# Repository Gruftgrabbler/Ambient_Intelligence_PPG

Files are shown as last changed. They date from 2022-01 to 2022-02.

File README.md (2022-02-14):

# Venen Funktionsmessung mittels PPG
Bei der venösen Photoplethysmographie wird die Lichtreflexion (Synonym: Licht-Reflexions-Rheographie, LRR)
mittels eines PPG-Sensors gemessen. Da Licht von Blut stärker als vom Gewebe absorbiert wird, nimmt
die Lichtreflexion bei steigendem Blutvolumen im Bein ab. Das LRR-Signal spiegelt daher Blutvolumenschwankungen wider.
Das LRR-Signal gliedert sich in einen gleich bleibenden Anteil durch Lichtabsorption in nicht-durchblutetem Gewebe 
(ca. 90 %), eine variable Lichtabsorption durch das venöse Blutvolumen (ca. 10 %) und eine periodische arterielle 
Lichtabsorption (ca. 0,5 %). Mithilfe digitaler Filtertechniken können diese Signale voneinander getrennt werden 
(digitale Photoplethysmographie, dPPG) [[1]](https://docplayer.org/21805396-Phlebologische-funktionsdiagnostik.html).

## Durchführung der Messung

Der sitzende Patient führt acht Dorsalextensionen im Sprunggelenk innerhalb von 16 Sekunden im Metronomrhythmus durch. Die Ferse ist dabei am Boden
abgestützt. Der PPG-Sensor wird mithilfe des 3D gedruckten Gehäuses ca. 10 cm oberhalb des Malleolus medialis angebracht (Abbildung 1). 

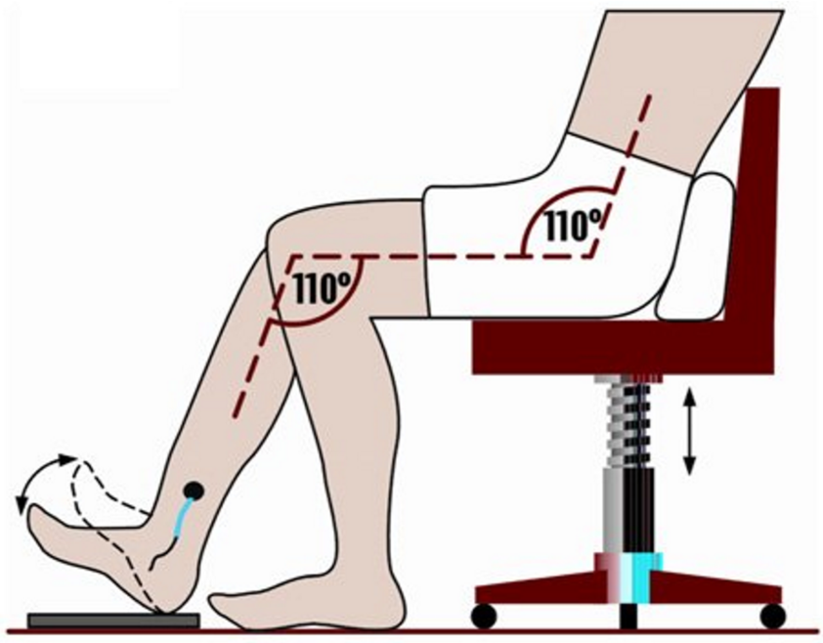
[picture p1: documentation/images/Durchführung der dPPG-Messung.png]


**Abbildung 1:** empfohlene Körperhaltung während der Messdurchführung [[2]](https://www.researchgate.net/publication/6482990_Photoplethysmography_and_its_application_in_clinical_physiological_measurement)

Die Fußbewegung führt zur Kompression der Beinvenen und damit zu einem Bluttransport nach proximal (Muskelpumpe). Das abnehmende Blutvolumen
spiegelt sich in der LRR-Kurve durch eine zunehmende Lichtreflexion wider (Abbildung 2). Nach Beendigung der Fußbewegungen fließt das 
Blut wieder nach distal. Bei insuffizienten Venen geschieht das schneller, als bei suffizienten Venenklappen 
[[1]](https://docplayer.org/21805396-Phlebologische-funktionsdiagnostik.html).

Mustermessung

**Abbildung 2:** LRR-Kurve mit zunehmender Lichtreflexion während der Fußbewegungen  [[3]](https://link.springer.com/chapter/10.1007/978-3-642-23804-8_36)[[4]](https://link.springer.com/chapter/10.1007/978-3-642-01709-4_35)

Der Messzyklus läuft vollautomatisch ab, die Messsignale werden ebenfalls automatisch ausgewertet.
Erfasst werden folgende Parameter zur unterstützenden Diagnostik der Venenfunktion:
* Venöse Wiederauffüllzeit 
* Venöse Halbwertszeit 
* Initiale Auffüllzeit 
* Venöse Pumpleistung 
* Venöse Pumparbeit 

## Konfiguration des MAX30102-Sensors

Der MAX30102 PPG-Sensor enthält zwei Leuchtdioden (LEDs), eine infrarote LED (Spitzenwellenlänge 880 nm) und eine rote LED (Spitzenwellenlänge 660 nm); dazu kommt eine Fotodiode, die spezifisch für Wellenlängen zwischen 600 und 900 nm ausgelegt ist. Im MAX30102 Sensor ist ein integrierter Temperatursensor zur Messung von Temperaturschwankungen, ein Analog-Digital Wandler (ADC) und eine I2C-Schnittstelle. Durch die Integration des ADC und der I2C-Schnittstelle in den Sensor selbst werden Rauschen und Artefakte, die zwischen der Fotodiode und dem ADC entstehen, auf ein Minimum reduziert. Die Daten werden über eine serielle Verbindung vom ESP32 an den angeschlossenen PC übertragen. Der PPG-Sensor wurde auf eine Abtastrate von 20 Hz konfiguriert, wobei die in Tabelle 1 aufgeführten Einstellungen verwendet wurden.

**Tabelle 1:** Empfohlene Einstellungen zur Konfiguration des MAX30102-Sensors
|    Setting    |      Value     | Description                                                                                                                        |
|---------------|:--------------:|------------------------------------------------------------------------------------------------------------------------------------|
| ledBrightness | 0x66 (= 20 mA) | Wertebereich (Hex-Dec=LED-Strom): 0-0=0mA (Off) to 0xFF-255=50mA <br /> 0x33-51=10mA. 0x66-102=20mA. 0x99-153=30mA. 0xCC-204=40mA  |
| sampleAverage |        4       | Averages multiple samples then draw once, reduce data throughput, default 4 samples average                                        |
| ledMode       |        1       | 1 = Red only, 2 = Red + IR, 3 = Red + IR + Green                                                                                   |
| sampleRate    |      1000      | Valid options: 50, 100, 200, 400, 800, 1000, 1600, 3200                                                                            |
| pulseWidth    |       411      | Valid options: 69, 118, 215, 411. The longer the pulse width, the wider the detection range. Default to be Max range               |
| adcRange      |      2048      | ADC Measurement Range, default 4096 (nA)，15.63(pA) per LSB at 18 bits resolution                                                  |

Die aufgeführten Werte wurden anhand des Datenblatts zum MAX30102 Sensor ermittelt und experimentell anhand einer ausreichenden Signalqualität bestätigt [[5]](https://pdfserv.maximintegrated.com/en/an/AN6409.pdf).

Bei der LRR-Messung wird die variable Lichtabsorption durch Schwankungen im venösen Blutvolumen gemessen. Daher ist für die Aufzeichnung der LRR-Kurve hauptsächlich das desoxygenierte Blut, bzw. die Absorption des Lichts durch desoxygenierte Hämoglobin von Relevanz. Dieses weist seine höchste Absorption im Wellenlängenbereich von 660-680 nm auf.
Aus diesem Grund wird für die LRR-Messung nur die rote LED des MAX30102 Sensors verwendet.

Abbildung 3 zeigt die zulässigen Einstellungen für die Messung der Blutvolumenschwankungen im Einzel-LED-Modus (Herzfrequenzmodus). Im Herzfrequenzmodus wird nur die rote LED verwendet, um optische Daten zu erfassen und die Herzfrequenz und/oder das Photoplethysmogramm (PPG) des Patienten zu bestimmen. Die grau hinterlegten Felder entsprechen den Einstellungen, die nicht zulässig sind. Der Benutzer sollte die Impulsbreite und die Abtastungen pro Sekunde anpassen, um die besten Einstellungen für seine Anwendung und den zulässigen Energieverbrauch zu ermitteln.

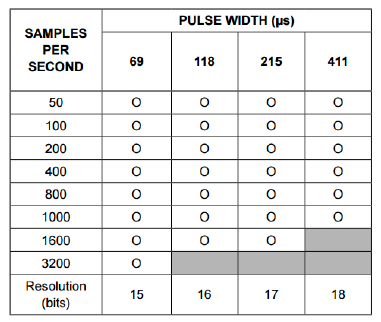
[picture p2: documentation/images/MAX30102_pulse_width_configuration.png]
pulse_width_configuration


**Abbildung 3:** Zulässige Einstellungen für die Pulsweiten-Konfiguration im Einzel-LED Betrieb (Herzfrequenzmodus). [[5]](https://pdfserv.maximintegrated.com/en/an/AN6409.pdf)

Die Pulsweite gibt an, wie lange das Abtastsignal aktiv ist. Je länger das Signal aktiv bleibt, desto mehr Energie wird verbraucht. Die Ansteuerungsfrequenz für die LEDs wird durch die Abtastrate bestimmt. Eine höhere Abtastrate führt zu einer höheren Ansteuerungsfrequenz und damit zu einem höheren Energieverbrauch. Die ideale Option für eine Wearable-Anwendung ist die Wahl einer geringeren Pulsbreite in Kombination mit einer geringeren Abtastrate, um den Energieverbrauch zu minimieren. Dies funktioniert jedoch nur bis zu einer gewissen Grenze, da die Pulsweite in einem umgekehrten Verhältnis zur Abtastrate steht. Dies ergibt sich aus der Überlegung, dass eine höhere Impulsbreite einer niedrigeren Antriebsfrequenz entspricht und umgekehrt. 

In unserem Anwendungsfall ist der Energieverbrauch des Sensors unerheblich, da der Sensor nicht in einer Wearable-Anwendung mit begrenzter Energieversorgung eingesetzt wird, sondern über die Energiezufuhr vom ESP32 bzw. vom PC gespeist wird. 

Im Datenblatt zu den empfohlenen Konfigurationen zum Betrieb des MAX30102 wird empfohlen, den ADC auf seinen höchsten Gain (= Verstärkungseinstellung) zu setzen (full-scale range = 2,048 μA). Wenn der Kanal gesättigt ist, muss die Verstärkungseinstellung auf den nächst höheren Wert eingestellt werden. [[6]](https://www.maximintegrated.com/en/products/interface/sensor-interface/MAX30102.html)

Der Sensor wird zur Befestigung am Bein in einem 3D gedruckten Gehäuse untergebracht (Abbildung 4). Anschließend wird ein Klettverschlussband oder ein dehnfähiges Band durch die Halterungsschlaufe hindurchgeführt und der Sensor wie in der Versuchsdurchführung beschrieben am Bein befestigt. Hierbei ist auf einen lockeren und nicht zu festen Anpressdruck zu achten!

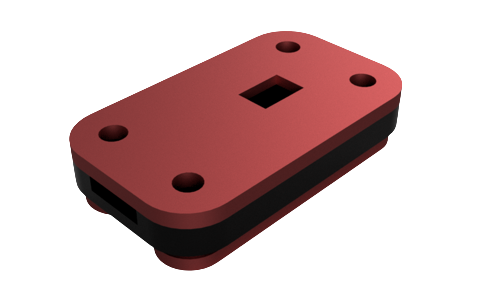
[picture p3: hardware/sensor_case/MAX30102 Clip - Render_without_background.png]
MAX30102 Clip - Render


**Abbildung 4:** Rendering des CAD Designs vom MAX30102 Clip zur Befestigung am Bein.

## Datenaufnahme
Zur Aufnahme und Speicherung der seriell übertragenen Messwerte durch den ESP32 wurde ein Python-Skript geschrieben (`real_time_plotter.py`). Der Python-Code erfasst die Daten und stellt diese in einem Echtzeit-Plotter grafisch dar. Zeitgleich werden die Messwerte direkt nach dem Empfang in einer *.csv-Datei gespeichert, was als Grundlage der nachfolgenden Analyse dient. 
Der Grund für die umgehende Datensicherung liegt in der hohen Eingangsgeschwindigkeit der Daten, welche mit einer Aufnahmefrequenz von 20 Hz eintreffen. Um die Datenverarbeitung zwischen den seriellen Erfassungen auf ein Minimum zu reduzieren, findet die weitere Datenverarbeitung nicht in Echtzeit, sondern im Anschluss an die Messung anhand der aufgezeichneten Messwerte in der csv-Datei statt.

## Vorverarbeitung der Daten
Für den Import der Messdaten aus der resultierenden CSV-Datei und die anschließende Datenverarbeitung zur Analyse wurde ein zweites Skript geschrieben (`plot_csv.py`). Der erste Schritt bei der Verarbeitung der LRR-Daten besteht darin, die Basislinie unserer Messdaten zu ermitteln. Hierfür betrachten wir die Ableitung erster Ordnung und ermitteln den Startzeitpunkt der Fußbewegungen anhand des Kurvenanstiegs über einen experimentell ermittelten Grenzwert hinaus. Der letzte Zeitpunkt vor dem Überschreiten des Grenzwerts wird als Startzeitpunkt der Messdurchführung definiert, die zugehörige Signalamplitude als Basislinie.

Im nächsten Schritt werden die Daten durch einen Tiefpass 4. Ordnung gefiltert. Die untere Grenzfrequenz wurde auf 3 Hz gewählt, um die Gleichstromkomponente der Daten zu entfernen. Anschließend werden die Zeitpunkte und Amplituden der lokalen Maxima mit der in Scipy integrierten Funktion *findpeaks* ermittelt. Für die weitere Analyse ist nur der zuletzt aufgetretene Höhepunkt nach Belastungsstop  von Relevanz. In Abbildung 5 ist eine Messdurchführung mit relevanten Punkten für die weitere Analyse dargestellt.

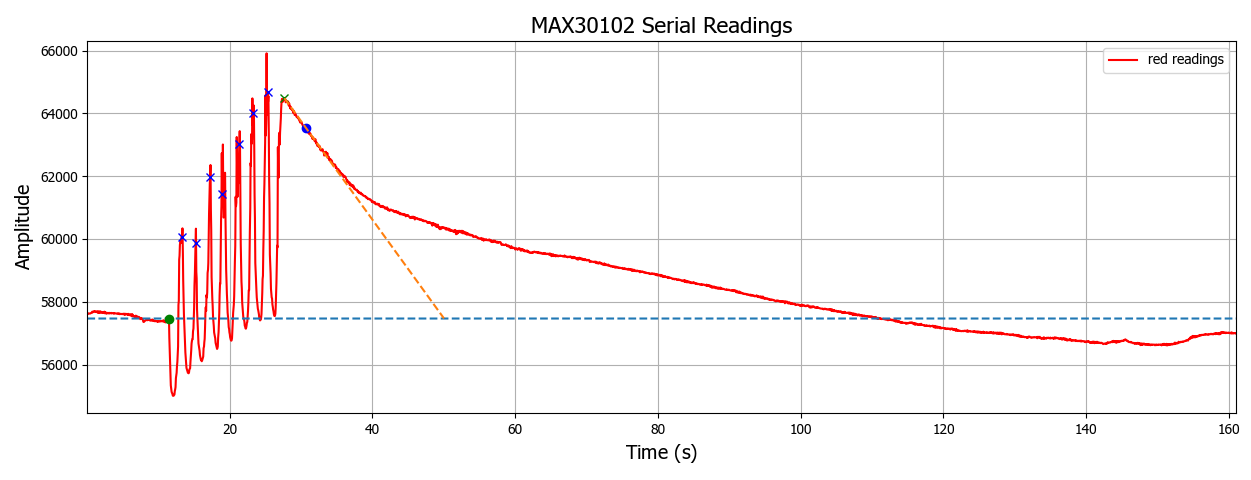
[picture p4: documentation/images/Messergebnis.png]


**Abbildung 5:** Messdurchführung mit relevanten Punkten

## Auswertung der Messergebnisse 
Die Berechnung der erfassten Messparameter ist der Fachliteratur entnommen [[7]](https://www.thieme-connect.de/products/ebooks/lookinside/10.1055/b-0034-8814)[[8]](https://eref.thieme.de/cockpits/clNuN0001clHAM0004/0/coNuN00260/4-910)[[9]](http://www.medpool.ch/geschuetzt/ch_seiten/med_300_/med_s123.htm)[[10]](http://docplayer.org/19942299-Dynamische-venenfunktionstests-auf-dem-pruefstand.html):

1. Aus dem Zeitintervall zwischen  und dem Ende des Kurvenabfalls am Schnittpunkt mit der Basislinie ergibt sich die venöse Auffüllzeit.

2. Aus dem Zeitintervall zwischen  und dem Unterschreiten von 50% der Amplitude von  ergibt sich die venöse Halbwertszeit.

3. Eine Gerade zwischen  und dem Kurvenpunkt nach drei Sekunden Abfall wird bis zur Basislinie verlängert und ergibt dort im Schnittpunkt die initiale Auffüllzeit.

4. Die venöse Pumpleistung folgt aus der Signalamplitude, nachdem die Signalamplitude mit der Amplitude der Basislinie normiert wurde:

      

5. Die venöse Pumparbeit wird durch Integration der venösen Pumpleistung über das Zeitintervall zwischen  und dem Ende des Kurvenabfalls am Schnittpunkt mit der Basislinie ermittelt.

In Tabelle 2 sind die ermittelten quantitativen Parameter für das Messsignal in Abbildung 5 gelistet.

**Tabelle 2:** ermittelte Parameter aus der automatisierten Analyse der aufgezeichneten Messwerte 
| Quantitative Parameter        | Messwerte |
|-------------------------------|:---------:|
| Venöse Auffüllzeit T_0 (s)    |    83.157 |
| Venöse Halbwertszeit T_50 (s) |    14.098 |
| Initiale Auffüllzeit T_i (s)  |    22.357 |
| Venöse Pumpleistung V_0 (%)   |    12.203 |
| Venöse Pumparbeit F_0 (%s)    |   311.642 |

# Setup

## Hardware

* Adafruit HUZZAH32 – ESP32 Feather Board oder ein alternativer Microcontroller mit I2C-Bus Ansteuerung
* MAX30102 Heart Rate/SpO2 Sensor
* 3D gedrucktes Gehäuse zur Befestigung des Sensors am Bein

## Software

* SparkFun MAX3010x Sensor Library für die Datenaufnahme
* Python 3.8 für die weitere Datenverarbeitung

## Getting Started

Stelle zunächst sicher, dass Python 3.8 auf dem Rechner installiert ist.

1. Best practice: Erstelle ein neues Virtual Environment, beispielsweise unter Verwendung von Anaconda oder PyCharm
2. Pullen des Repository einschließlich der Submodule: `git submodule update --init --recursive`
3. Installiere die Projekt-Requirements mittels pip: `pip install -r requirements.txt`

### Anleitung zur Messdurchführung
1. Drucke das Gehäuse des PPG-Sensors mit einem 3D-Drucker aus und setze den MAX30102-Sensor ein. Führe anschließend ein Klettverschlussband oder ein dehnfähiges Band durch die Halterungsschlaufe hindurch und befestige den Sensor wie in der Versuchsdurchführung beschrieben am Bein. Hierbei ist auf einen lockeren und nicht zu festen Anpressdruck zu achten!
2. Stelle eine Hardware Verbindung zwischen dem MAX30102-Sensor und dem ESP32 her
3. Flashe den ESP32 mit der *MAX30102_Basic_Readings.ino* im Projektordner *embedded/arduino-sketches/MAX30102_Basic_Readings/*
4. Führe das Skript `real_time_plotter.py` im Projektordner *src/serial/serial_plotter/* in der Python IDE deiner Wahl aus. Es öffnet sich eine GUI mit den Messsignalen der roten und infraroten LEDs. Zur problemlosen Analyse der Messdaten wird empfohlen, dass nur ein einziger vollständiger Messdurchgang pro csv-Datei gespeichert wird. Dies wird durch Beenden des Skripts nach Abschluss der Messung erreicht.
5. Führe zur Bestimmung der diagnostisch relevanten quantitativen Parameter das Skript `lrr_signal_evaluation.py` im *src/* Ordner aus. Sofern die Messung vorher korrekt durchgeführt wurde, gibt das Skript die gesuchten Parameter in der Konsole aus und stellt das Messsignal mitsamt einigen relevanten Punkten grafisch dar.

# Literaturverzeichnis

[[1]](https://docplayer.org/21805396-Phlebologische-funktionsdiagnostik.html) Stücker, M. & Doerler, M. (2014). Phlebological functional diagnostics. Phlebologie, 43(05), 268–272. https://doi.org/10.12687/phleb2213-5-2014

[[2]](https://www.researchgate.net/publication/6482990_Photoplethysmography_and_its_application_in_clinical_physiological_measurement) Allen, John. (2007). Photoplethysmography and its application in clinical physiological measurement. Physiological Measurement. 28. R1-39. https://doi.org/10.1088/0967-3334/28/3/R01

[[3]](https://link.springer.com/chapter/10.1007/978-3-642-23804-8_36) Noppeney T. (2013) Varikose. In: Jauch KW., Mutschler W., Hoffmann J., Kanz KG. (eds) Chirurgie Basisweiterbildung. Springer, Berlin, Heidelberg. https://doi.org/10.1007/978-3-642-23804-8_36

[[4]](https://link.springer.com/chapter/10.1007/978-3-642-01709-4_35) Noppeney T., Nüllen H. (2012) Varikose der unteren Extremität. In: Debus E., Gross-Fengels W. (eds) Operative und interventionelle Gefäßmedizin. Springer, Berlin, Heidelberg. https://doi.org/10.1007/978-3-642-01709-4_35

[[5]](https://pdfserv.maximintegrated.com/en/an/AN6409.pdf) MAX3010x EV Kits: Recommended Configurations and Operating Profiles. (2018b, Juni 27). Maxim Integrated - Analog, Linear, and Mixed-Signal Devices. Abgerufen am 9. Februar 2022, von https://www.maximintegrated.com/en/design/technical-documents/userguides-and-manuals/6/6409.html

[[6]](https://www.maximintegrated.com/en/products/interface/sensor-interface/MAX30102.html) MAX30102 High-Sensitivity Pulse Oximeter and Heart-Rate Sensor for Wearable Health. (2020, 13. Februar). Maxim Integrated - Analog, Linear, and Mixed-Signal Devices. Abgerufen am 9. Februar 2022, von https://www.maximintegrated.com/en/products/interface/sensor-interface/MAX30102.html

[[7]](https://www.thieme-connect.de/products/ebooks/lookinside/10.1055/b-0034-8814) Rabe, E. & Gerlach, H. E. (Hrsg.). (2006). 3.4 Photoplethysmographie. In: Praktische Phlebologie - Empfehlungen zur differenzierten Diagnostik und Therapie phlebologischer Krankheitsbilder, (2. vollständig überarbeitete Auflage Thieme Verlagsgruppe, Stuttgart, New York, Delhi, Rio), 38–40. https://doi.org/10.1055/b-0034-8814

[[8]](https://eref.thieme.de/cockpits/clNuN0001clHAM0004/0/coNuN00260/4-910) Ludwig M, Rieger J, Ruppert V. Auswertung. In: Ludwig M, Rieger J, Ruppert V, Hrsg. Gefäßmedizin in Klinik und Praxis. 2., komplett überarbeitete und aktualisierte Auflage. Stuttgart: Thieme; 2010. https://doi.org/10.1055/b-002-10340

[[9]](http://www.medpool.ch/geschuetzt/ch_seiten/med_300_/med_s123.htm) Wosnitzka, H. (o. D.). PPG-Parameter bei CVI-Verlaufskontrolle – aus einer Pharmakotherapiestudie. medpool.ch. Abgerufen am 9. Februar 2022, von http://www.medpool.ch/geschuetzt/ch_seiten/med_300_/med_s123.htm

[[10]](http://docplayer.org/19942299-Dynamische-venenfunktionstests-auf-dem-pruefstand.html) Häfner, H. M., Bablich, H., Rassner, G., Jünger, M. & Steins, A. (2002). Dynamische Venenfunktionstests auf dem Prüfstand. Phlebologie, 31(04), 85–90. https://doi.org/10.1055/s-0037-1621393

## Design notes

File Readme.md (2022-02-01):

# Venen Funktionsmessung mittels PPG
Bei der venösen Photoplethysmographie wird die Lichtreflexion (Synonym: Licht-Reflexions-Rheographie, LRR)
mittels eines PPG-Sensors gemessen. Da Licht von Blut stärker als vom Gewebe absorbiert wird, nimmt
die Lichtreflexion bei steigendem Blutvolumen im Bein ab. Das PPG-Signal spiegelt daher Blutvolumenschwankungen wider.
Das PPG-Signal gliedert sich in einen gleich bleibenden Anteil durch Lichtabsorption in „undurchblutetem“ Gewebe 
(ca. 90 %), eine variable Lichtabsorption durch das venöse Blutvolumen (ca. 10 %) und eine periodische arterielle 
Lichtabsorption (ca. 0,5 %). Mithilfe digitaler Filtertechniken können diese Signale voneinander getrennt werden 
(digitale Photoplethysmographie, dPPG) [[1]](https://docplayer.org/21805396-Phlebologische-funktionsdiagnostik.html).

## Durchführung der Messung

Der sitzende Patient führt acht Dorsalextensionen im Sprunggelenk innerhalb von 16 Sekunden im Metronomrhythmus durch. Die Ferse ist dabei am Boden
abgestützt. Der PPG-Sensor wird mithilfe des 3D gedruckten Gehäuses ca. 10 cm oberhalb des Malleolus medialis angebracht (Abbildung 1). 



**Abbildung 1:** Empfohlene Körperhaltung während der Messdurchführung [[2]](https://www.researchgate.net/publication/6482990_Photoplethysmography_and_its_application_in_clinical_physiological_measurement)

Die Fußbewegung führt zur Kompression der Beinvenen und damit zu einem Bluttransport nach proximal (Muskelpumpe). Das abnehmende Blutvolumen
spiegelt sich in der PPG-Kurve durch eine zunehmende Lichtreflexion wider (Abbildung 2). Nach Beendigung der Fußbewegungen fließt das 
Blut wieder nach distal. Bei insuffizienten Venen geschieht das schneller, als bei suffizienten Venenklappen 
[[1]](https://docplayer.org/21805396-Phlebologische-funktionsdiagnostik.html).

Mustermessung

**Abbildung 2:** PPG-Kurve mit zunehmender Lichtreflexion während der Fußbewegungen  [[3]](https://link.springer.com/chapter/10.1007/978-3-642-23804-8_36)

Der Messzyklus läuft vollautomatisch ab, die Messsignale werden ebenfalls automatisch ausgewertet.
Erfasst werden folgende Parameter zur unterstützenden Diagnostik der Venenfunktion:
* Venöse Wiederauffüllzeit 
* Venöse Halbwertszeit 
* Initiale Auffüllzeit 
* Venöse Pumpleistung 
* Venöse Pumparbeit 

## Konfiguration des MAX30102-Sensors

Der MAX30102 PPG-Sensor enthält zwei Leuchtdioden (LEDs), eine infrarote LED (Spitzenwellenlänge 880 nm) und eine rote LED (Spitzenwellenlänge 660 nm); dazu kommt eine Photodiode, die spezifisch für Wellenlängen zwischen 600 und 900 nm ausgelegt ist. Im MAX30102 Sensor ist ein integrierter Temperatursensor zur Messung von Temperaturschwankungen, ein Analog-Digital Wandler (ADC) und eine I2C-Schnittstelle. Durch die Integration des ADC und der I2C-Schnittstelle in den Sensor selbst werden Rauschen und Artefakte, die zwischen der Fotodiode und dem ADC entstehen, auf ein Minimum reduziert. Die Daten werden über eine serielle Verbindung vom ESP32 an den angeschlossenen PC übertragen. Der PPG-Sensor wurde auf eine Abtastrate von 20 Hz konfiguriert, wobei die in Tabelle 1 aufgeführten Einstellungen verwendet wurden.

**Tabelle 1:** Empfohlene Einstellungen zur Konfiguration des MAX30102-Sensors
|    Setting    |      Value     | Description                                                                                                                        |
|---------------|:--------------:|------------------------------------------------------------------------------------------------------------------------------------|
| ledBrightness | 0x66 (= 20 mA) | Wertebereich (Hex-Dec=LED-Strom): 0-0=0mA (Off) to 0xFF-255=50mA <br /> 0x33-51=10mA. 0x66-102=20mA. 0x99-153=30mA. 0xCC-204=40mA  |
| sampleAverage |        4       | Averages multiple samples then draw once, reduce data throughput, default 4 samples average                                        |
| ledMode       |        3       | 1 = Red only, 2 = Red + IR, 3 = Red + IR + Green                                                                                   |
| sampleRate    |      1000      | Valid options: 50, 100, 200, 400, 800, 1000, 1600, 3200                                                                            |
| pulseWidth    |       411      | Valid options: 69, 118, 215, 411. The longer the pulse width, the wider the detection range. Default to be Max range               |
| adcRange      |      2048      | ADC Measurement Range, default 4096 (nA)，15.63(pA) per LSB at 18 bits resolution                                                  |

## Datenaufnahme
Zur Aufnahme und Speicherung der seriell übertragenen Messwerte durch den ESP32 wurde ein Python-Skript geschrieben (`real_time_plotter.py`). Der Python-Code erfasst die Daten und stellt diese in einem Echtzeit-Plotter graphisch dar. Zeitgleich werden die Messwerte direkt nach dem Empfang in einer .csv-Datei gespeichert, was als Grundlage der nachfolgenden Analyse dienst. 
Der Grund für die umgehende Datensicherung liegt in der hohen Eingangsgeschwindigkeit der Daten, welche mit einer Aufnahmefrequenz von 20 Hz eintreffen. Um die Datenverarbeitung zwischen den seriellen Erfassungen auf ein Minimum zu reduzieren, findet die weitere Datenverarbeitung nicht in Echtzeit, sondern im Anschluss an die Messung anhand der aufgezeichneten Messwerte in der csv-Datei statt.

## Vorverarbeitung der Daten
Für den Import der Messdaten aus der resultierenden CSV-Datei und die anschließende Datenverarbeitung zur Analyse wurde ein zweites Skript geschrieben (`plot_csv.py`). Der erste Schritt bei der Verarbeitung der PPG-Daten besteht darin, die Basislinie unserer Messdaten zu ermitteln. Hierfür betrachten wir die Ableitung erster Ordnung und ermitteln den Startzeitpunkt der Fußbewegungen anhand des Kurvenanstiegs über einen experimentell ermittelten Grenzwert hinaus. Der letzte Zeitpunkt vor dem Überschreiten des Grenzwerts wird als Startzeitpunkt der Messdurchführung definiert, die zugehörige Signalamplitude als Basislinie.

Im nächsten Schritt werden die Daten durch einen Tiefpass 4. Ordnung gefiltert. Die untere Grenzfrequenz wurde auf 3 Hz gewählt, um die Gleichstromkomponente der Daten zu entfernen. Anschließend werden die Zeitpunkte und Amplituden der lokalen Maxima mit der in Scipy integrierten Funktion *findpeaks* ermittelt. Für die weitere Analyse ist nur der zuletzt aufgetretene Höhepunkt nach Belastungsstop  von Relevanz. In Abbildung 3 ist eine Messdurchführung mit relevanten Punkten für die weitere Analyse dargestellt.

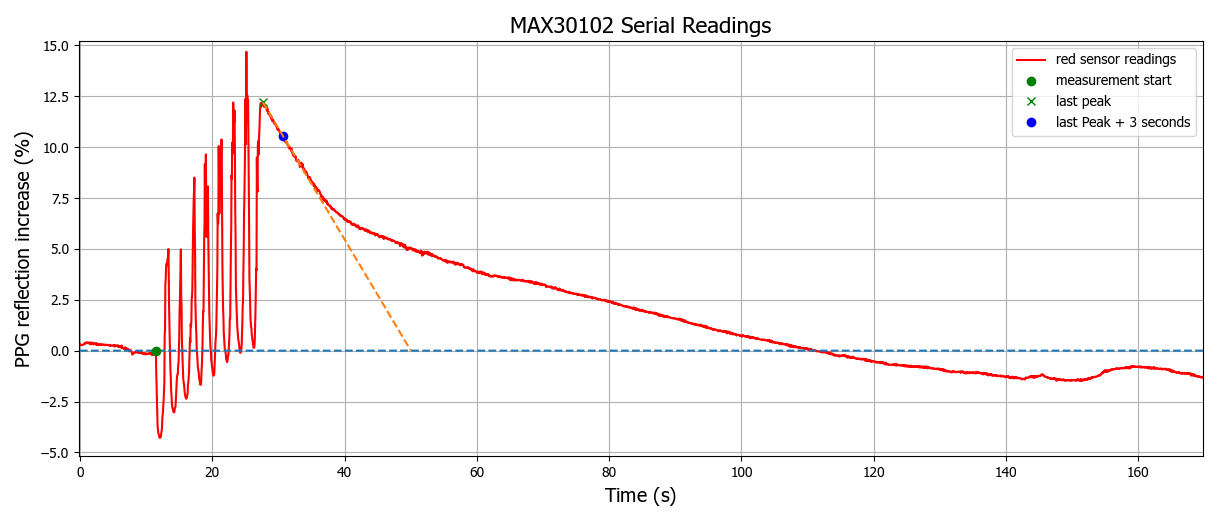
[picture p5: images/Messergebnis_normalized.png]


**Abbildung 3:** Messdurchführung mit relevanten Punkten

## Auswertung der Messergebnisse 
Aus dem Zeitintervall zwischen  und dem Ende des Kurvenabfalls am Schnittpunkt mit der Basislinie ergibt sich die venöse Auffüllzeit.

Aus dem Zeitintervall zwischen  und dem Unterschreiten von 50% der Amplitude von  ergibt sich die venöse Halbwertszeit.

Eine Gerade zwischen  und dem Kurvenpunkt nach drei Sekunden Abfall wird bis zur Basislinie verlängert und ergibt dort im Schnittpunkt die initiale Auffüllzeit.

Die venöse Pumpleistung folgt aus der Signalamplitude, nachdem es mit der Amplitude der Basislinie normiert wurde:


Die venöse Pumparbeit wird durch Integration der venösen Pumpleistung über das Zeitintervall zwischen  und dem Ende des Kurvenabfalls am Schnittpunkt mit der Basislinie ermittelt.

In Tabelle 2 sind die ermittelten quantitativen Parameter für das Messsignal in Abbildung 3 gelistet.

**Tabelle 2:** Ermittelte Parameter aus der automatisierten Analyse der aufgezeichneten Messwerte 
| Quantitative Parameter        | Messwerte |
|-------------------------------|:---------:|
| Venöse Auffüllzeit T_0 (s)    |    83.157 |
| Venöse Halbwertszeit T_50 (s) |    14.098 |
| Initiale Auffüllzeit T_i (s)  |    22.357 |
| Venöse Pumpleistung V_0 (%)   |    12.203 |
| Venöse Pumparbeit F_0 (%s)    |   311.642 |

# Setup

## Hardware

* Adafruit HUZZAH32 – ESP32 Feather Board
* MAX30102 Heart Rate/SpO2 Sensor
* 3D gedrucktes Gehäuse zur Befestigung des Sensors am Bein

## Software

* Sparkfun MAX3010x Sensor Library für die Datenaufnahme
* Python 3.8 für die weitere Datenverarbeitung

## Pull repository including submodules

```
 git submodule update --init --recursive
```

## Anleitung zur Messdurchführung
1. Drucke das Gehäuse des PPG-Sensors mit einem 3D-Drucker aus und setze den MAX30102-Sensor ein. Führe anschließend ein Klettverschlussband oder ein dehnfähiges Band durch die Halterungsschlaufe hindurch und befestige den Sensor wie in der Versuchsdurchführung beschrieben am Bein. Hierbei ist auf einen lockeren und nicht zu festen Anpressdruck zu achten!
2. Stelle eine Hardware Verbindung zwischen dem MAX30102-Sensor und dem ESP32 her
3. Flashe den ESP32 mit der *MAX30102_Basic_Readings.ino* im Projektordner *arduino-sketches/MAX30102_Basic_Readings/*
4. Installiere die Requirements für die python Skripte in der bevorzugten Python IDE mit:  
   `pip install -r requirements.txt`
5. Führe das Skript `real_time_plotter.py` in der Python IDE deiner Wahl aus. Es öffnet sich eine GUI mit den Messsignalen der roten und infraroten LEDs. Zur problemlosen Analyse der Messdaten wird empfohlen, dass nur ein einziger vollständiger Messdurchgang pro csv-Datei gespeichert wird. Dies wird durch Beenden des Skripts nach Abschluss der Messung erreicht.
6. Führe zur Bestimmung der diagnostisch relevanten quantitativen Parameter das Skript `plot_csv.py` aus. Sofern die Messung vorher korrekt durchgeführt wurde, gibt das Skript die gesuchten Parameter in der Konsole aus und stellt das Messsignal mitsamt einigen relevanten Punkten grafisch dar.

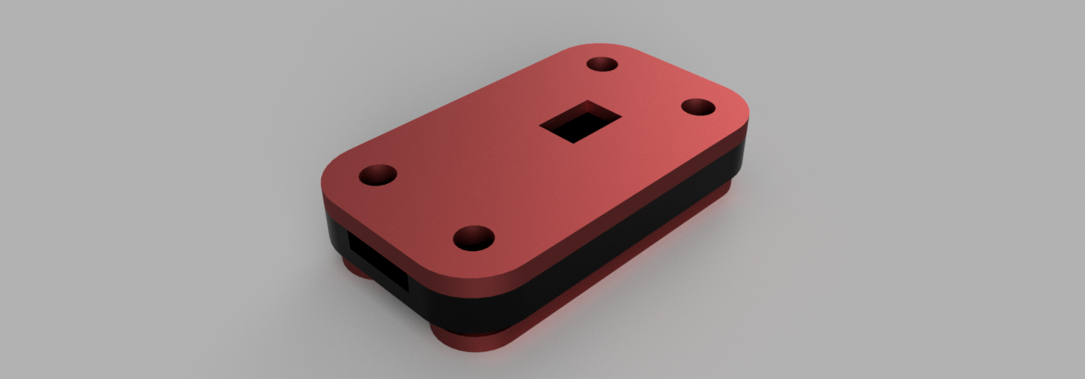
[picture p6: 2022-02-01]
hardware/sensor_case/MAX30102 Clip - Render.png

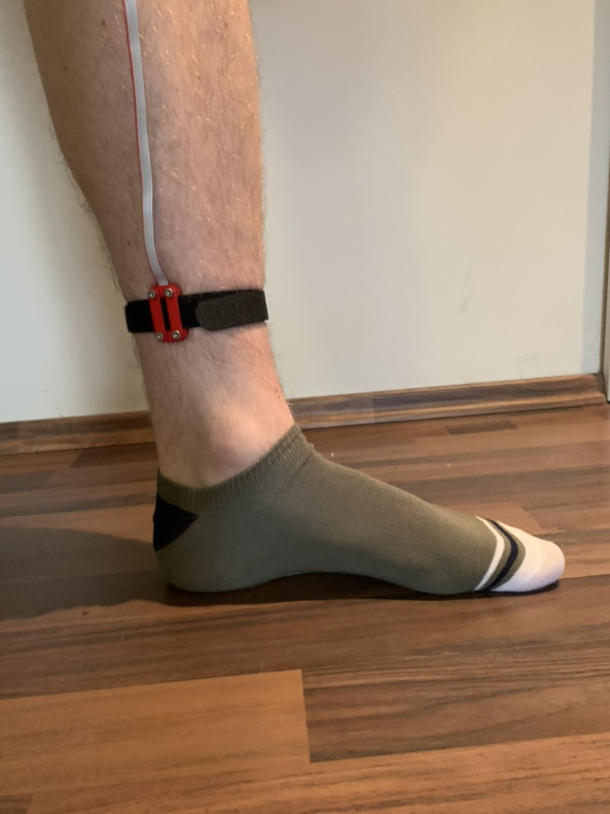
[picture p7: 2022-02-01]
documentation/images/Food-with-clip.jpeg

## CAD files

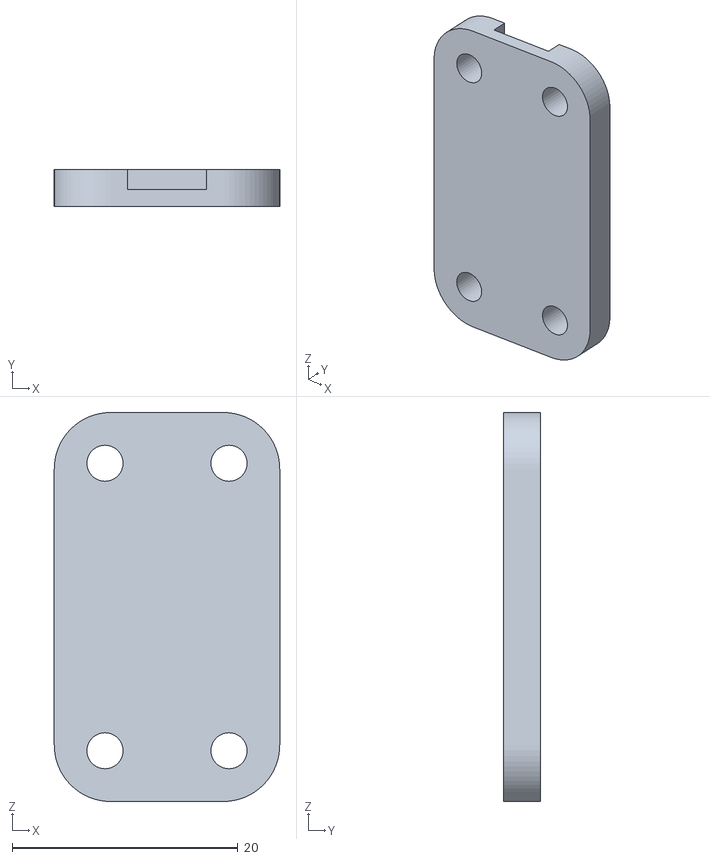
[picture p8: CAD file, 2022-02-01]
hardware/sensor_case/stl/SensorHolderBottom.stl
20.0 x 3.25 x 34.5

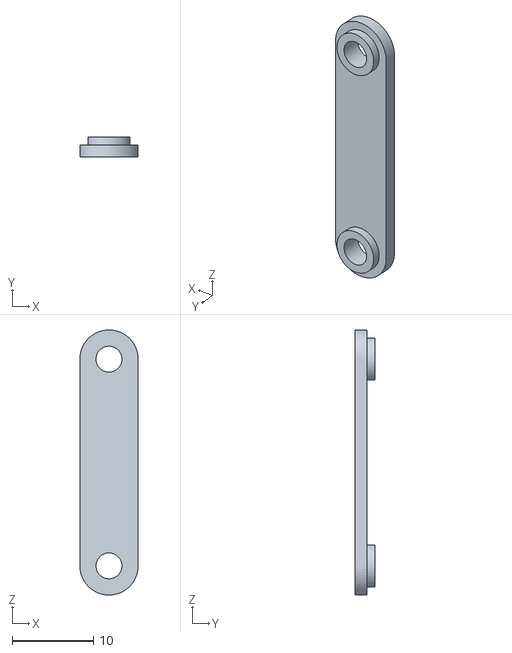
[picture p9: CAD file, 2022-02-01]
hardware/sensor_case/stl/Food 1.stl
7.20 x 2.50 x 32.7

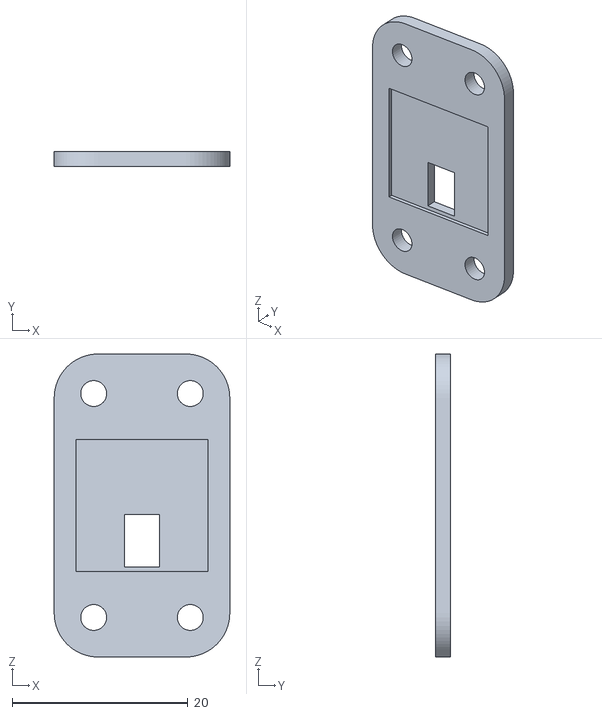
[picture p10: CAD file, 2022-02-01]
hardware/sensor_case/stl/SensorHolderTop.stl
20.0 x 1.75 x 34.5

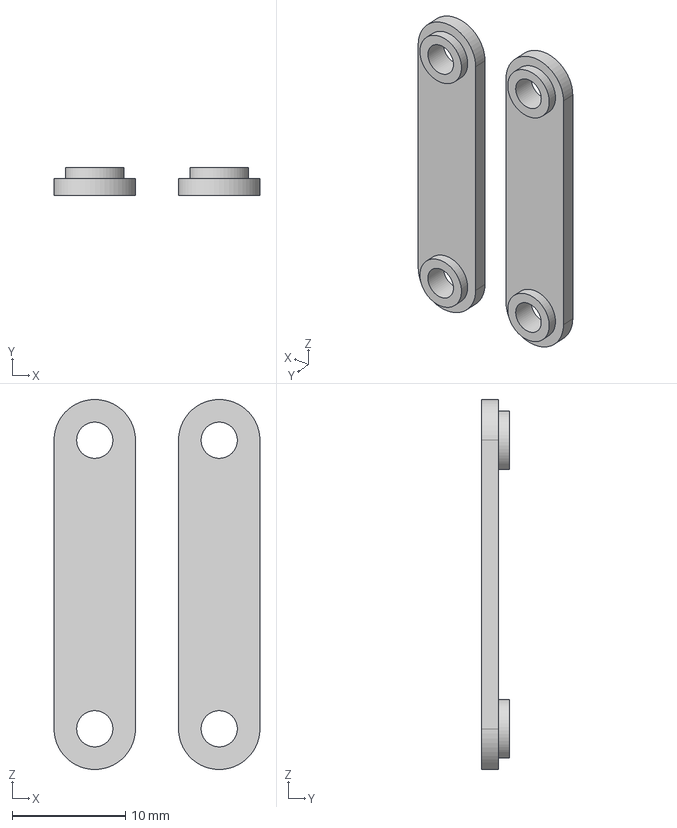
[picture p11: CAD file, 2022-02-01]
hardware/sensor_case/step/MAX30102 Clip - Food 1.step
18.2 x 2.50 x 32.7 mm

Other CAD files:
hardware/sensor_case/stl/Food 2.stl
hardware/sensor_case/step/MAX30102 Clip - Sensor Holder Top.step
hardware/sensor_case/step/MAX30102 Clip - Food 2.step
hardware/sensor_case/step/MAX30102 Clip - Sensor Holder Bottom.step

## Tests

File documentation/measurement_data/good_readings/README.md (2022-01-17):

data3.csv und data4.csv beinhalten eine einzelne sehr schöne Messung

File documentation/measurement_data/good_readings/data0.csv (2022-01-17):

Millis | Red | IR
320281 | 98705 | 123610
320332 | 98661 | 123585
320391 | 98620 | 123550
320434 | 98602 | 123559
320485 | 98605 | 123588
320536 | 98666 | 123605
320590 | 98660 | 123589
320638 | 98636 | 123571
320689 | 98542 | 123534
320751 | 98530 | 123529
320791 | 98548 | 123541
320842 | 98548 | 123542
320893 | 98530 | 123550
320951 | 98508 | 123521
320996 | 98450 | 123468
321047 | 98414 | 123550
321098 | 98371 | 123433
321151 | 98382 | 123470
321200 | 98439 | 123518
321251 | 98486 | 123499
321310 | 98454 | 123498
321353 | 98418 | 123474
321404 | 98425 | 123489
321455 | 98450 | 123509
321510 | 98456 | 123510
321557 | 98447 | 123506
321608 | 98448 | 123474
321671 | 98331 | 123408
321710 | 98267 | 123389
321761 | 98212 | 123359
321812 | 98181 | 123308
321870 | 98297 | 123630
321914 | 98650 | 123353
321965 | 97955 | 123238
322016 | 98075 | 123253
322070 | 97994 | 123266
322118 | 98145 | 123405
322170 | 98254 | 123409
322231 | 98243 | 123398
322272 | 98207 | 123351
322323 | 98140 | 123306
322374 | 97974 | 123230
322431 | 97980 | 123262
322476 | 98024 | 123262
322527 | 98032 | 123281
322578 | 97924 | 123192
322631 | 97872 | 123208
322680 | 97937 | 123281
322731 | 98010 | 123263
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

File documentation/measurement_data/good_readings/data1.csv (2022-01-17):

Millis | Red | IR
589924 | 86169 | 112592
589976 | 86173 | 112576
590034 | 86152 | 112578
590080 | 86169 | 112570
590132 | 86155 | 112561
590194 | 86157 | 112557
590237 | 86150 | 112544
590289 | 86160 | 112522
590341 | 86157 | 112503
590394 | 86151 | 112511
590445 | 86163 | 112494
590497 | 86169 | 112485
590554 | 86151 | 112491
590601 | 86161 | 112467
590653 | 86168 | 112461
590713 | 86173 | 112473
590757 | 86165 | 112477
590809 | 86171 | 112474
590862 | 86162 | 112450
590914 | 86167 | 112420
590966 | 86156 | 112428
591018 | 86151 | 112400
591073 | 86165 | 112399
591122 | 86167 | 112380
591174 | 86165 | 112383
591233 | 86167 | 112368
591278 | 86171 | 112395
591330 | 86170 | 112347
591382 | 86171 | 112337
591434 | 86172 | 112340
591487 | 86178 | 112335
591539 | 86182 | 112327
591594 | 86177 | 112320
591643 | 86177 | 112326
591695 | 86188 | 112313
591754 | 86194 | 112297
591799 | 86181 | 112272
591851 | 86182 | 112285
591903 | 86155 | 112255
591955 | 86174 | 112269
592007 | 86194 | 112265
592059 | 86164 | 112241
592113 | 86165 | 112250
592164 | 86198 | 112268
592216 | 86150 | 112241
592275 | 86143 | 112243
592320 | 86198 | 112240
592372 | 86160 | 112238
592435 | 86143 | 112236
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

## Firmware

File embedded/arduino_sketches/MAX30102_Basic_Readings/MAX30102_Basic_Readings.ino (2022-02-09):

/*
  MAX30105 Breakout: Output all the raw Red/IR/Green readings
  By: Nathan Seidle @ SparkFun Electronics
  Date: October 2nd, 2016
  https://github.com/sparkfun/MAX30105_Breakout

  Outputs all Red/IR/Green values.

  Hardware Connections (Breakoutboard to Arduino):
  -5V = 5V (3.3V is allowed)
  -GND = GND
  -SDA = A4 (or SDA)
  -SCL = A5 (or SCL)
  -INT = Not connected

  The MAX30105 Breakout can handle 5V or 3.3V I2C logic. We recommend powering the board with 5V
  but it will also run at 3.3V.

  This code is released under the [MIT License](http://opensource.org/licenses/MIT).
*/

/*
  NOTE:

  This is a modified version of the Example1_Basic_Readings from the Sparkfun MAX30102 Library.
  This version will meassure the time since the meassurements starts and count the meassured samples.
  It will print the serial data in the format:
  millis, ir, red, sample

  Additionally it has an extra function pollSerial which polls from the Serial input.
  On the computer there might be a python script running which wants to reset the meassurement.
*/

#include <Wire.h>
#include "MAX30105.h"

MAX30105 particleSensor;
unsigned long t_run;
unsigned long t_start;
unsigned int n_samples;

#define debug Serial //Uncomment this line if you're using an Uno or ESP
//#define debug SerialUSB //Uncomment this line if you're using a SAMD21

void setup()
{

  pinMode(LED_BUILTIN, OUTPUT);
  digitalWrite(LED_BUILTIN, LOW);

  debug.begin(9600);

  // Initialize sensor
  if (particleSensor.begin() == false)
  {
    debug.println("MAX30105 was not found. Please check wiring/power. ");
    while (1);
  }

    //Let's configure the sensor to run fast so we can over-run the buffer and cause an interrupt
  byte ledBrightness = 0x66; //Options: 0=Off to 255=50mA
  byte sampleAverage = 4; //Options: 1, 2, 4, 8, 16, 32
  byte ledMode = 1; //Options: 1 = Red only, 2 = Red + IR, 3 = Red + IR + Green
  byte sampleRate = 1000; //Options: 50, 100, 200, 400, 800, 1000, 1600, 3200
  int pulseWidth = 411; //Options: 69, 118, 215, 411
  int adcRange = 2048; //Options: 2048, 4096, 8192, 16384
  particleSensor.setup(ledBrightness, sampleAverage, ledMode, sampleRate, pulseWidth, adcRange); //Configure sensor with these settings

  n_samples = 0;
  t_start = millis();
}

// Polls the serial port and restart messaruement
void pollSerial() {

  if (debug.available()) {
    int reading = Serial.readString().toInt();

    if (reading == 0)
      digitalWrite(LED_BUILTIN, HIGH);
    delayMicroseconds(10);
    digitalWrite(LED_BUILTIN, LOW);

    // Start the meassurement again.
    t_start = millis();
    n_samples = 0;
  }
}

void loop()
{
  pollSerial();
  t_run = millis() - t_start;
  debug.print("Millis=");
  debug.print(t_run);
  debug.print(",Red=");
  debug.print(particleSensor.getRed());
  debug.print(",IR=");
  debug.print(particleSensor.getIR());
  debug.print(",samples=");
  debug.print(n_samples++);
  debug.println();
}

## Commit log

2021-12-02 Uploaded Arduino File: MAX30102_B
2021-12-05 added simple prototype of live plot using matplotlib (runs slowly)
2021-12-05 added simple prototype of live plot using pyqtgraph (runs smooth)
2021-12-10 added esp32 ddetection for windows
2022-01-14 Upload Meassurements
    [data0.csv, data1.csv, data2.csv, data3.csv]
2022-01-14 added data3.csv and data4.csv
    [data3.csv, data4.csv]
2022-01-14 Sauber durchgeführte einzelne Mustermessung
    [reading_14-01-2022_11-32-24.csv, reading_14-01-2022_11-53-52.csv]
2022-01-14 modify data1.csv
    [data1.csv]
2022-01-18 erweiterung um lineare approximationsgerade und peak detection
2022-01-18 Erweiterung um Funktionalität des dynamischen Plottens
2022-01-25 - renamed ende_kurvenabfall to end_intersection
    - added alternative way to print values in a pretty table (import of tabulate package required)
2022-01-25 - added calculation of venous pump function by integrating the signal
    - renamed ende_kurvenabfall to end_intersection
    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
2022-02-01 - fixed a few typos in printed parameters
2022-02-01 added mechanical design files to repo
    [Food 1.stl, Food 2.stl, MAX30102 Clip - Food 1.step, MAX30102 Clip - Food 2.step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]
2022-02-03 - clean up: refactor code parts into seperate modules; introduce a new folder structure; add type annotations where possible; implement suggestions of the ci tools - ci / gh actions: add a GitHub Act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
    [Food 1.stl, Food 2.stl, MAX30102 Clip - Food 1.step, MAX30102 Clip - Food 2.step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]
2022-02-09 update Arduino File MAX30102_Basic_Readings.ino to current sensor settings
